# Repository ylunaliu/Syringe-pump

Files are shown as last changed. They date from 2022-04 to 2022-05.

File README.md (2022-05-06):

# Syringe pump
Upright syringe pump for laboratory fluidics. 10ml/30ml

# Commercial parts:
Linear stage: https://www.amazon.ca/dp/B09J4FRZQM/ref=sspa_dk_detail_0?pd_rd_r=6cb2d65c-4c96-45af[…]FpbCZhY3Rpb249Y2xpY2tSZWRpcmVjdCZkb05vdExvZ0NsaWNrPXRydWU&th=1 

Motor: https://www.amazon.ca/Twotrees-Stepper-42BYGH-Degree-Printer/dp/B08C28V44F/ref=sr_1[…]or%2525252Bnema%2525252B17%2525252Caps%2525252C286&sr=8-6&th=1

Motor driver: https://www.amazon.ca/TB6600-Stepper-Driver-Controller-tb6600/dp/B07B9ZQF5D/ref=sr_[…]45839654&sprefix=tb6600%25252525252Caps%25252525252C115&sr=8-2

Microswitch: https://leeselectronic.com/en/product/3804-micro-switch-spdt-short-roller-12a-125v-v-12-fl22-c1.html Disclaimer: Our switch holder is specfically design for this switch, if you are using a different switch the part needs to be redesign for switch-holder-top and siwtch-holder-bottom.

# Communication Protocol

So as we design the communication protocol, we need to send strings via serial communication. The functions that we need include:

**set_volume**: Set the volume of the fluid in the syringe

**set_flowrate**: Set the flow rate of the fluid in the syringe

**push**: Push from the syringe pump

**draw**: draw from the syringe pump 

**stop**: Stop the syringe pump

**whoami**: checking the identity of the pump (10ml or the 30ml pump)

**get_status**: 

state = 0: idle, not doing anything, stopped.

state = 1: The pump is currently drawing

state = 2: The pump is currently pushing

# Command sent from MATLAB/Serial monitor:

We decided on the serial command that was being sent from MATLAB should have the format of “string, the number”. Basically is a string of word comma numbers. The word here is to select functions and the number is for volume and flowrate. 

For example, if we want to set the volume as 2ml (need to convert to microliter) for the 10ml pump the serial command would be 

“setvolume,2000”

As another example, if we want to call other functions that don’t require a second argument as a number(let’s say it’s the push function), it would be

“push,“

# Conversion for the flowrate:

6400 steps per revolution, with 8mm per revolution for the lead screw. So every step moves 0.00125mm.

6mm = 1000ul (We measured this);1ul = 6/1000 mm

1step = 0.00125mm; 1mm = 800 steps

Flowrate is in ul/minutes

So the delay time in Arduino would be

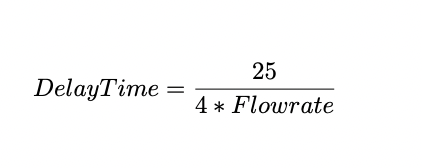
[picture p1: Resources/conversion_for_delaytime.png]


The whole calculatioin for the conversion for the flowrate goes here



The steps that's required to push thourgh the volume is:



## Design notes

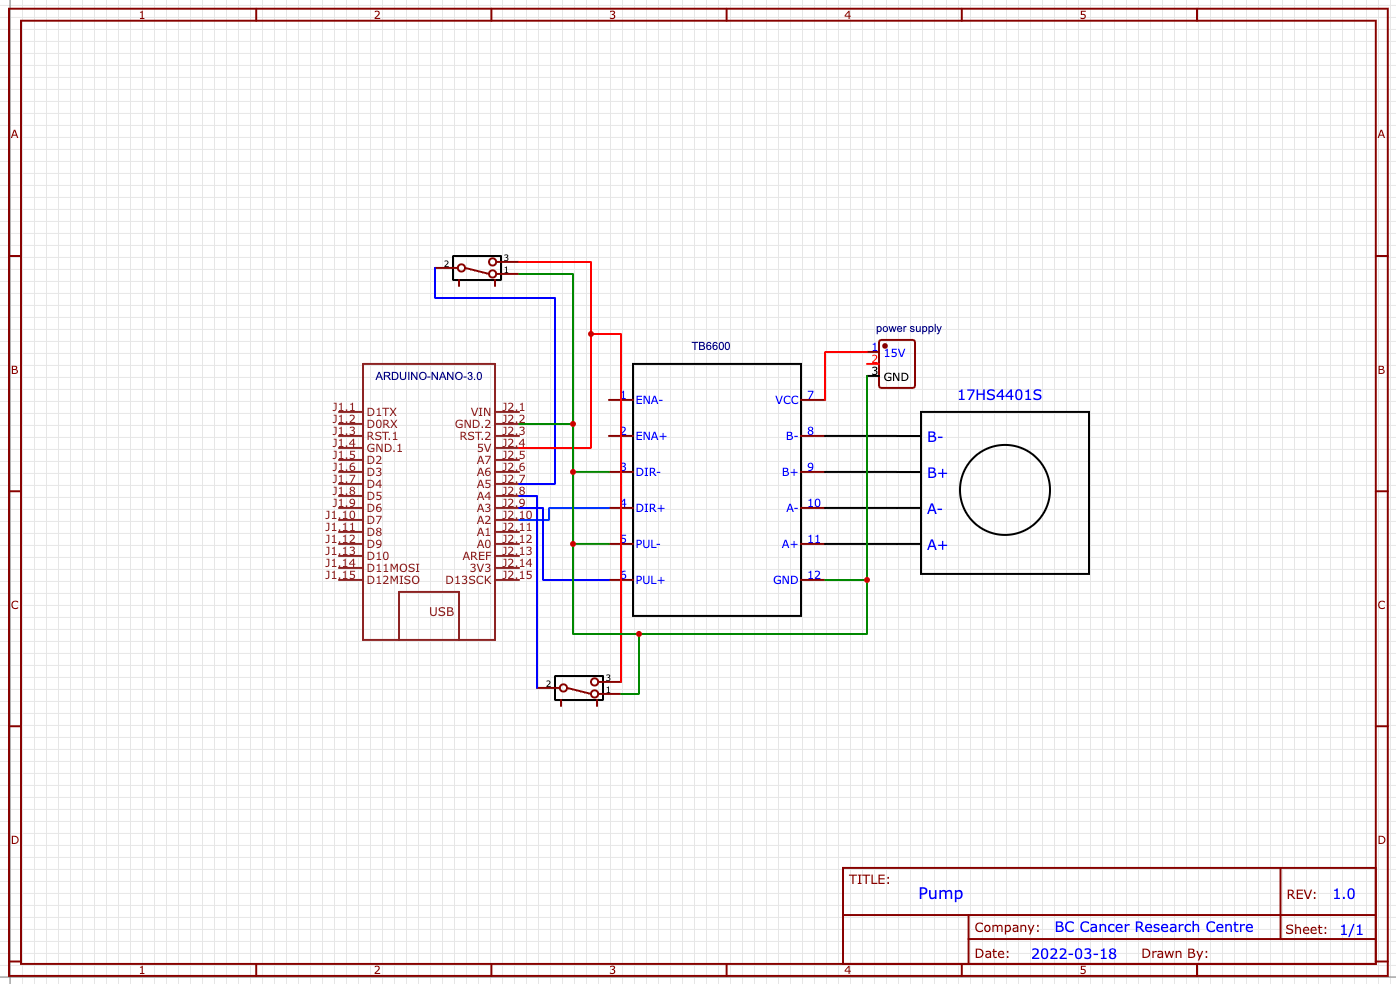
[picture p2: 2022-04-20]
Circuit diagram/circuit diagram.png

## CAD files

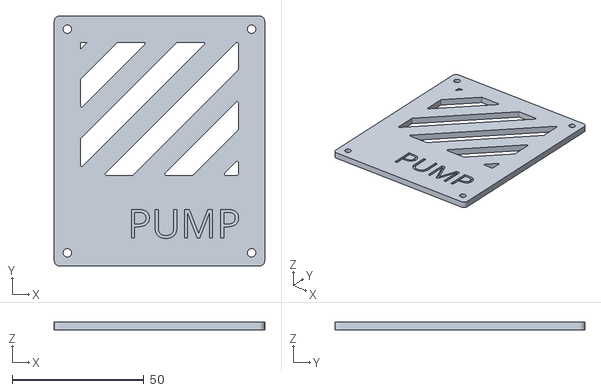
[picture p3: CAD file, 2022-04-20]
CAD STL file/housing/housing-top.stl
80.0 x 95.0 x 3.00

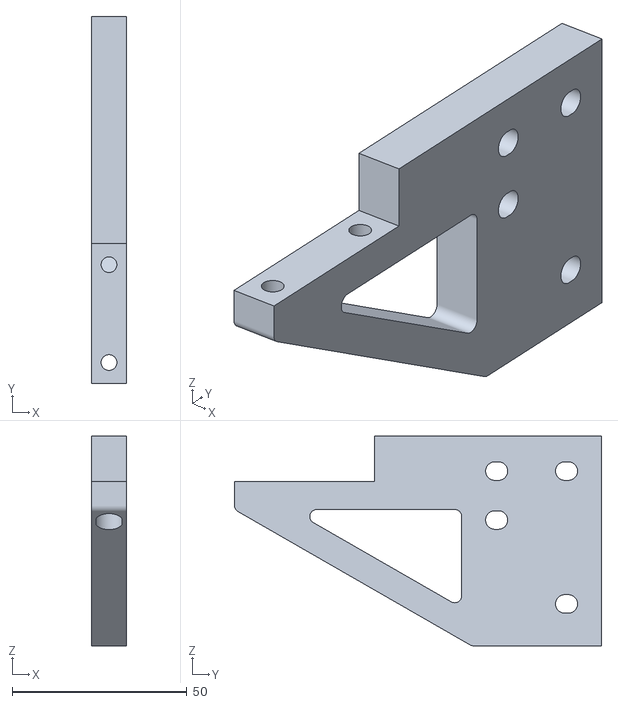
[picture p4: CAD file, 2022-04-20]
CAD STL file/lower-syringe-holder/side.stl
10.0 x 105.0 x 60.0

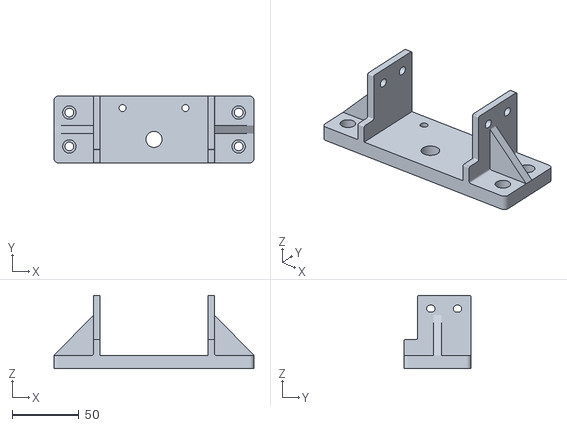
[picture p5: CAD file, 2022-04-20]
CAD STL file/stage-bottom.stl
150.0 x 50.0 x 55.0

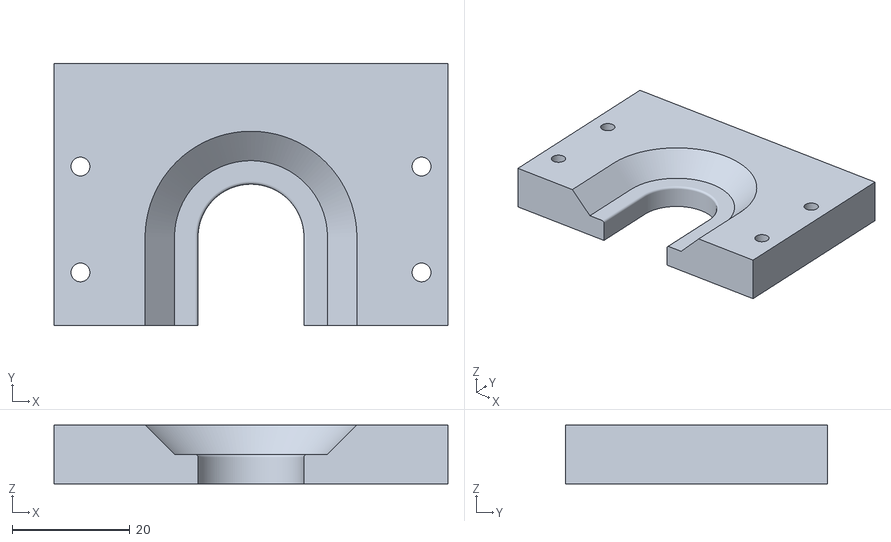
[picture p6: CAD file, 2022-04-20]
CAD STL file/upper-syringe-holder/bottom-30ml.stl
67.0 x 44.5 x 10.0

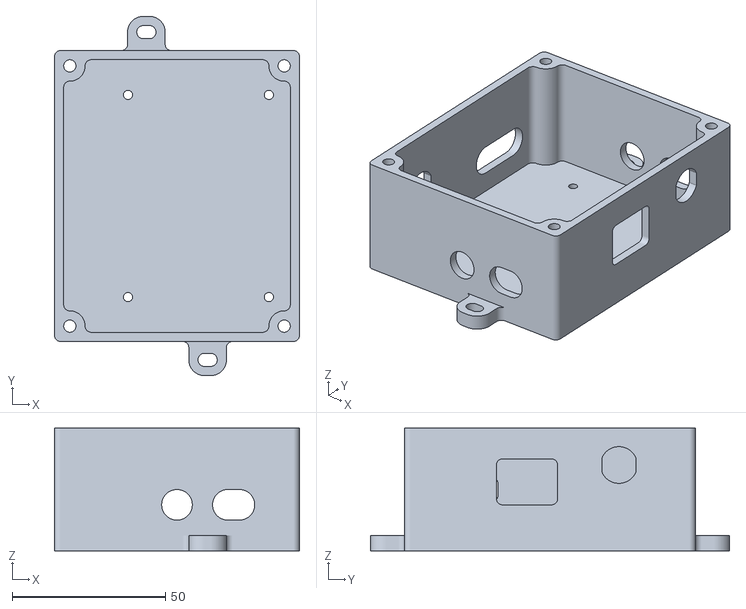
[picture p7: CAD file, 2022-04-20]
CAD STL file/housing/housing-bottom.stl
80.0 x 117.3 x 40.0

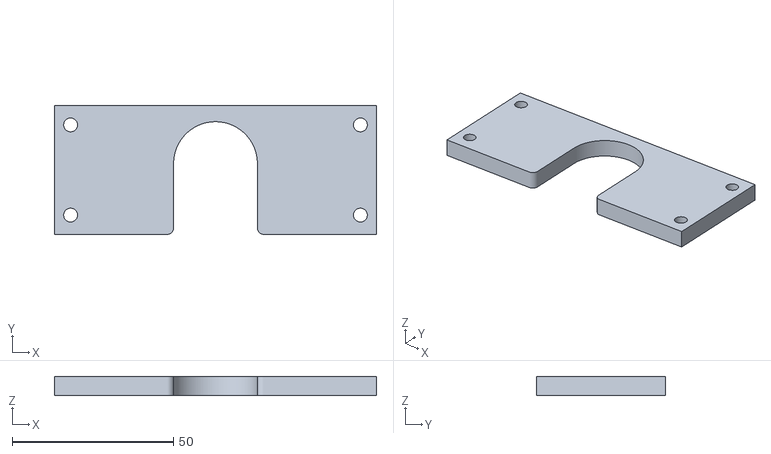
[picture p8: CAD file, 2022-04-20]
CAD STL file/lower-syringe-holder/top-30ml.stl
100.0 x 40.0 x 6.00

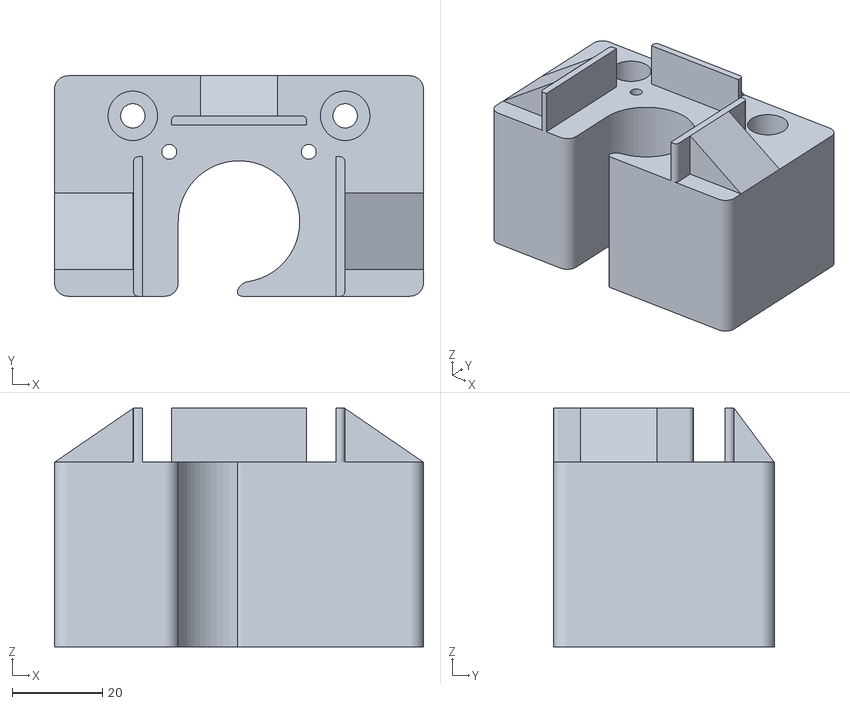
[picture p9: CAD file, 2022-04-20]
CAD STL file/Motor_cap.stl
82.0 x 49.0 x 53.0

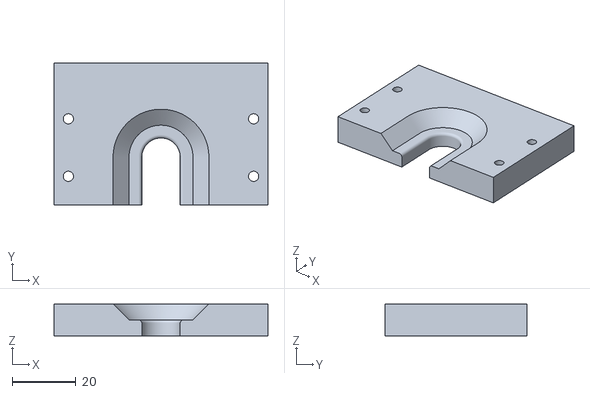
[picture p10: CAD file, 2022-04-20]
CAD STL file/upper-syringe-holder/bottom-10ml.stl
67.0 x 44.5 x 10.0

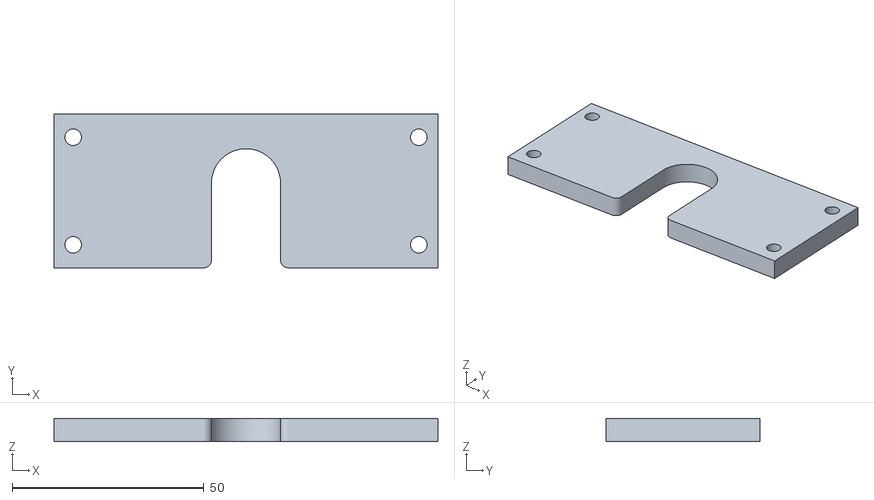
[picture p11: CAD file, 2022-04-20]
CAD STL file/lower-syringe-holder/top-10ml.stl
100.0 x 40.0 x 6.00

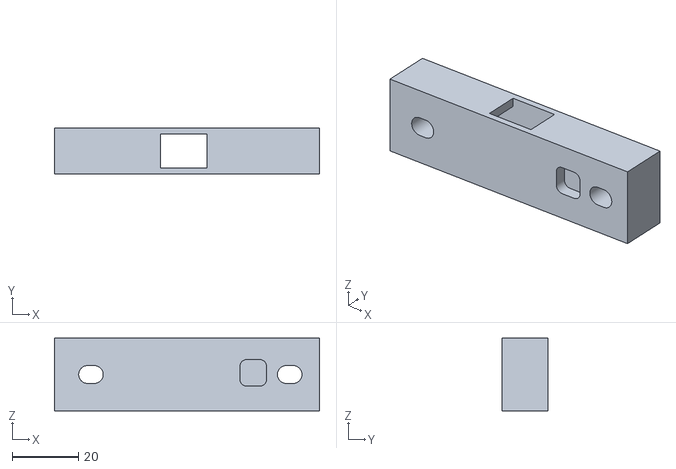
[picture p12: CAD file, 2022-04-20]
CAD STL file/switch-holder-bottom.stl
80.0 x 14.0 x 22.0

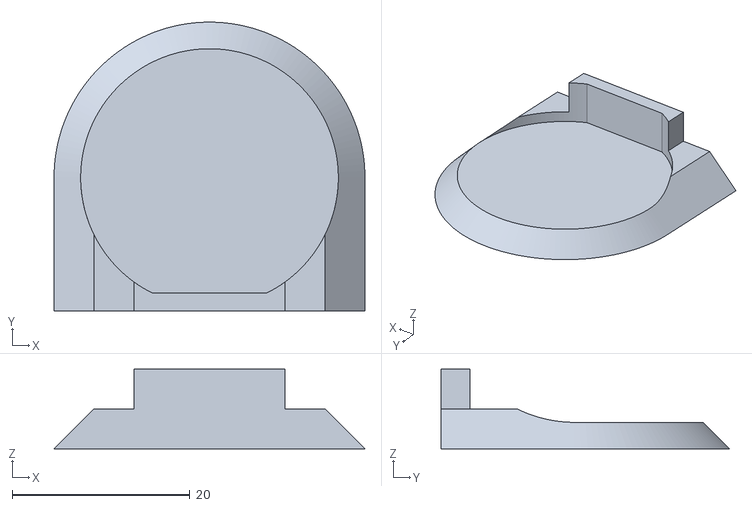
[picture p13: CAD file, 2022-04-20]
CAD STL file/upper-syringe-holder/slider-30ml.stl
35.0 x 32.5 x 9.00

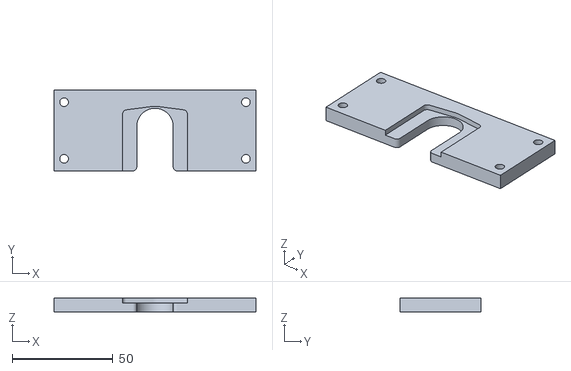
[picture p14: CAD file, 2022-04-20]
CAD STL file/lower-syringe-holder/bottom-10ml.stl
100.0 x 40.0 x 7.00

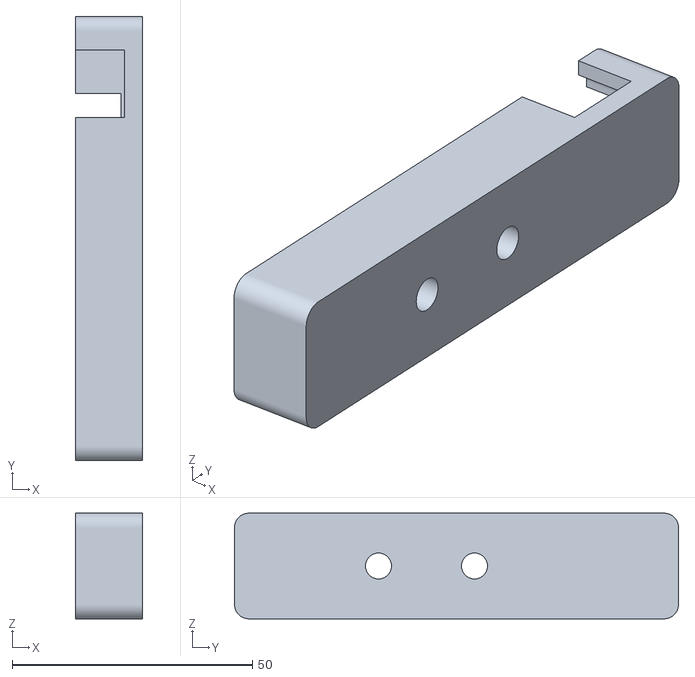
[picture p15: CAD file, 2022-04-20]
CAD STL file/switch-holder-top.stl
14.0 x 92.5 x 22.0

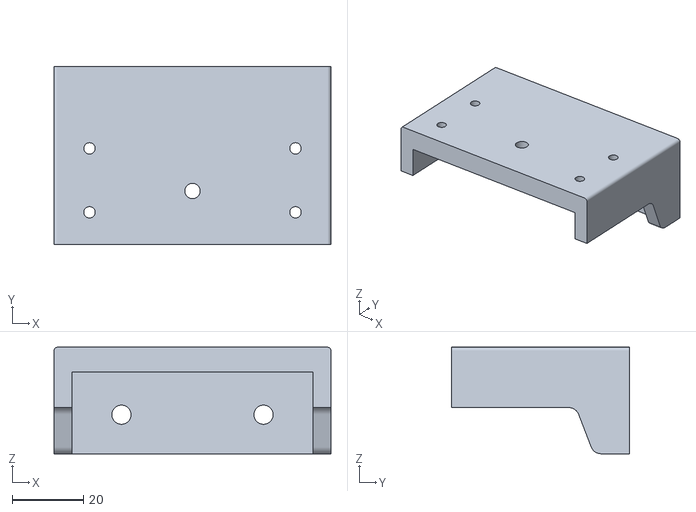
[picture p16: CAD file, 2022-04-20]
CAD STL file/upper-syringe-holder/top.stl
78.0 x 50.0 x 30.0

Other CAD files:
CAD STL file/lower-syringe-holder/bottom-30ml.stl
CAD STL file/upper-syringe-holder/slider-10ml.stl

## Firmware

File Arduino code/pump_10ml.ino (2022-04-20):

//Define useful parameter here
#define dirPin 2
#define stepPin 3
#define switchUp 4
#define switchDown 5
String inputString = ""; //string holding the incoming data
String command; //String that stores the command (setVol, setflow, getStatus, Stop, Push, Draw, whoami)
float commandval; //stores the speed or flowrate
boolean stringComplete = false; //whether the string is complete
float flowrate = 800; 
float volume = 300; 
boolean posDirection = true; //direction for the pump
int delimiterIndex[2];
int state = 0; //state of the pump
int steps = 0; // should get updated when stop/push/draw command comes in and while running in loop
float delaytime = 2;

void setup() {
  // put your setup code here, to run once:
  Serial.begin(9600);
  inputString.reserve(100);
  pinMode(stepPin, OUTPUT);
  pinMode(dirPin, OUTPUT);
  pinMode(switchUp, INPUT);
  pinMode(switchDown, INPUT);

  //Set the spinning direction cw/ccw
  digitalWrite(dirPin, HIGH);
  
}


void serialEvent(){
  while(Serial.available()){
    // get the new byte
    char inChar = (char)Serial.read();
    // add it to the inputString
    inputString += inChar;
    // if the incoming character is a newline, set a flag
    // so the main loop can do something about it
    if(inChar == '\n'){
      stringComplete = true;
      }
    }
  }



void loop() {
  // print the string when a newline arrives:
  if(stringComplete){
    //find the delimiters and store them in a char array
    delimiterIndex[0] = inputString.indexOf(',');
    delimiterIndex[1] = inputString.indexOf(',', delimiterIndex[0]+1);
    
    // use the numbers stores in the char array to split the inputString into pieces.
    String command = inputString.substring(0, delimiterIndex[0]);
    String commandvalue = inputString.substring(delimiterIndex[0]+1, delimiterIndex[1]);

    commandval=commandvalue.toFloat();
    //clear the inputString
    inputString = "";
    //change the boolean state
    stringComplete = false;

    if(command == "setvolume"){
      Serial.print("set the volume to ");
      Serial.print(commandvalue);
      volume = commandval; 
      }

    if(command == "setflowrate"){
      Serial.print("set the flow rate to ");
      Serial.print(commandvalue);
      flowrate = commandval;
      delaytime = 25 / (4*flowrate)*1000;
      }
     
    if(command =="push"){
      Serial.println("Push pump");
      steps = 4.8*volume;
      state = 2;
      digitalWrite(dirPin, HIGH);
      }

    if(command == "draw"){
      Serial.print("Draw pump");
      steps = 4.8*volume;
      state = 1;
      digitalWrite(dirPin, LOW);
      }
    
    if(command == "stop"){
      Serial.print("Stop");
      steps = 0;
    //  Serial.print(steps);
      }
    
    if(command == "whoami"){
      Serial.print("I am the 10ml pump");
      }

    if(command == "getstatus"){
     // Serial.print("Status");
      Serial.println(state);
      }
  }
    
    //draw
    //precautionary measures for debouncing
    if((steps > 0) & (state==1)){
      if(digitalRead(switchUp)==HIGH){
        steps= 0;
        state = 0;
      }
      if(digitalRead(switchUp)==HIGH){
        steps= 0;
        state = 0;
      }
      digitalWrite(stepPin, HIGH);
      delay((int)delaytime);
      digitalWrite(stepPin, LOW);
      delay((int)delaytime);
      steps -= 1;
      }

    //push
    if((steps >0) & (state==2)){
      if(digitalRead(switchDown)==HIGH){
        steps= 0;
        state = 0;
      }
      if(digitalRead(switchDown)==HIGH){
        steps= 0;
        state = 0;
      }
      digitalWrite(stepPin, HIGH);
      delay((int)delaytime);
      digitalWrite(stepPin, LOW);
      delay((int)delaytime);
      steps -= 1;
      }    

}
